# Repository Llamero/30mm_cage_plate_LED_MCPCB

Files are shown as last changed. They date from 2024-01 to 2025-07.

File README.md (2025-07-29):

# 30 mm Cage Plate LED Driver
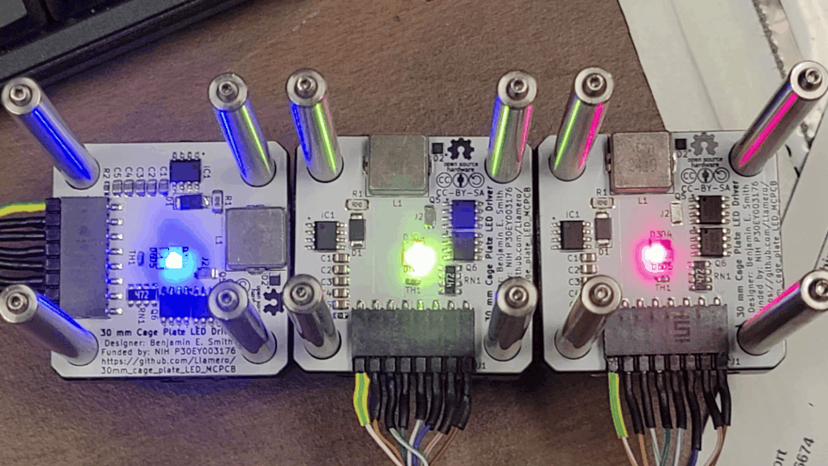
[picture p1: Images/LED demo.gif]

## 4x LED 30 mm Cage Plate Board Description:
This board is an entirely self-contained LED and driver circuitry designed to be compatible with the Thorlabs 30 mm cage plate system: https://www.thorlabs.com/navigation.cfm?guide_id=2004  

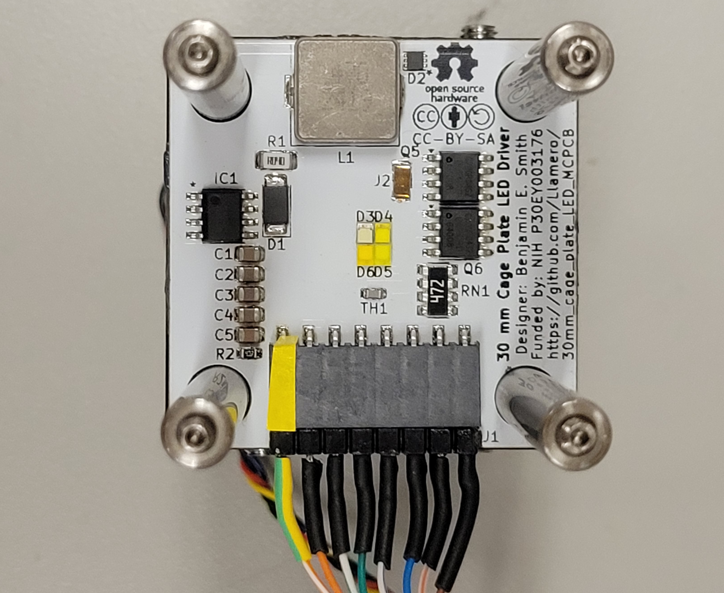
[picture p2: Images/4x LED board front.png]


The LEDs on the board are closely spaced so that all four LEDs efficiently couple into a 5 mm liquid light guide or other optical paths.

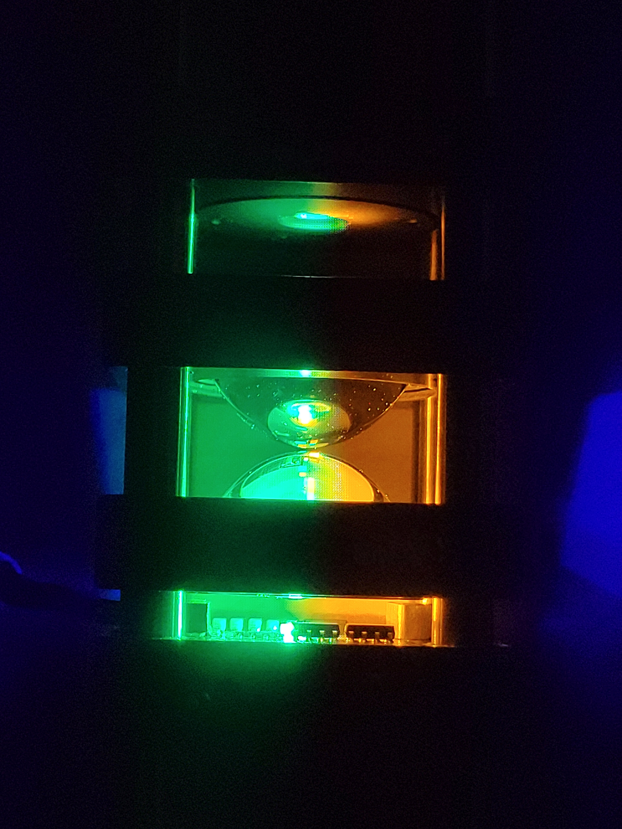
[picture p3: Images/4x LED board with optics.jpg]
Side view of LED with opticas


Each board can drive up to four individual LEDs, and includes a thermistor for temperature monitoring.  The the LED current is regulated by an [AL8843](https://www.diodes.com/part/view/AL8843), allowing LEDs to be driven with up to three amps of current.  The [AL8843](https://www.diodes.com/part/view/AL8843) also allows for both PWM control as well as analog current control down to 10% of the current limit (see below for setting max current limit).

Four p-channel mosfets on the board create a 1x4 multiplexer that allows individual LEDs to be toggled on by pulling the corresponding LED channel's gate to ground.  Each gate has a 4.7 kOhm pullup resistor so that each channel defaults to being off if not connected.

To turn the LEDs off more rapidly, there is also a 38V TVS diode parallel to the inductor that can be used to dump the residual energy stored in the inductor by setting all four multiplexer channels high.

A heatsink and fan can also be mounted to the backside of the cage plate for active cooling of high-current LEDs.

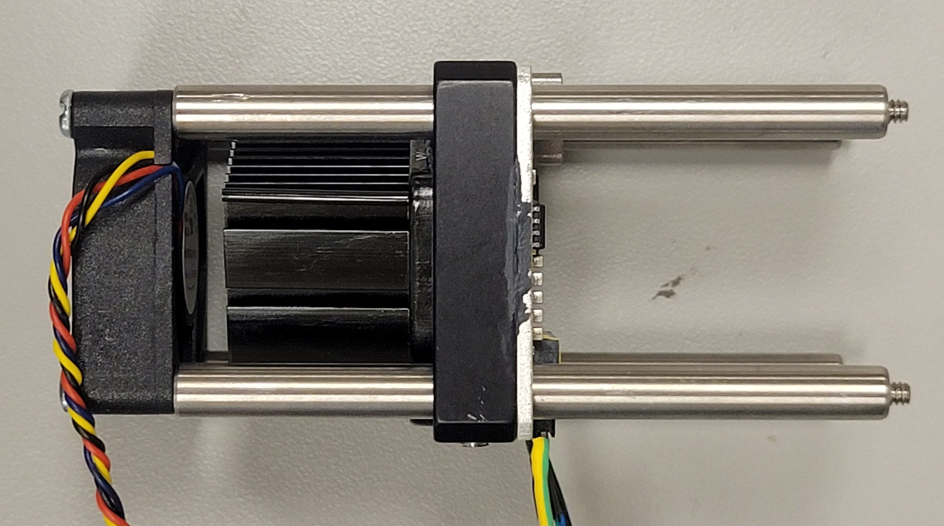
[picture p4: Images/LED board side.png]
Side view of LED driver

## 3x 30 mm Cage Plate Controller Description:
This repository also includes the design files for a controller that can operate up to three 30 mm cage plates for a total of 12 LEDs.

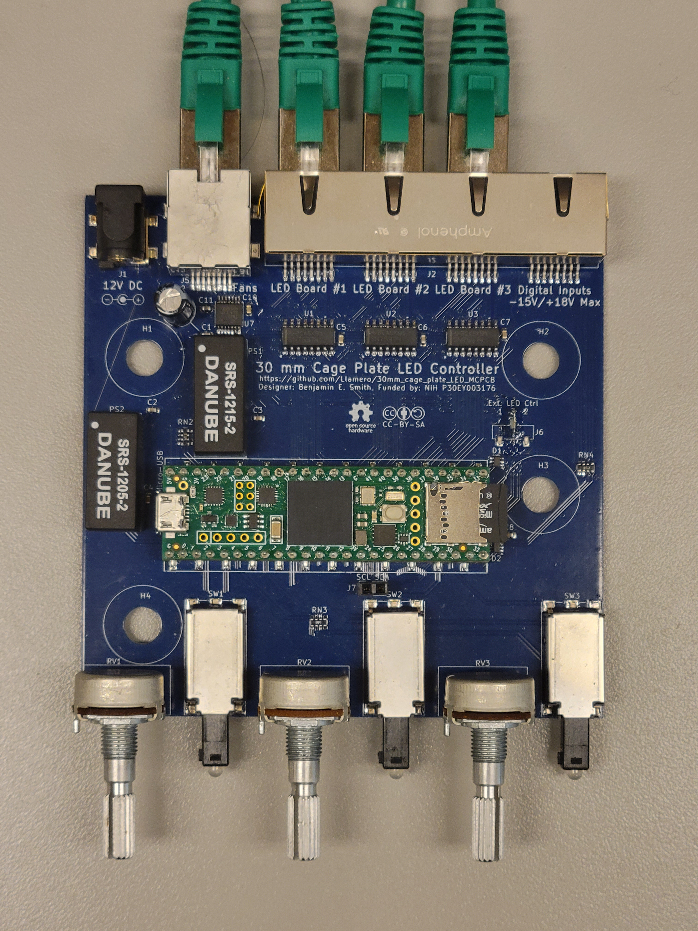
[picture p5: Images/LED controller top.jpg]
LED controller top


The controller is powered by a Teensy 4.1 which allows for precise timing control (<10 ns hysteresis) of each LED, as well a complex programmable control.  

On the back of the driver, each board connects to the driver via a shielded cat5 ethernet cable.  Additionally, there is a cat5 port with both a 12V supply and three channels of 5V PWM outputs for both powering the fans for each board as well as controlling the fan speed.  Finally, there are four protected digital inputs allowing for control signals up to -15V/+18V.

On the front of the driver, there is a potentiometer for controlling the intensity of each of the three LED boards, as well as a pushbutton to select the channel for each board.  Additionally, each pushbutton includes a red-green LED indicator to indicate which of the four LED channels is active.

## Driver Software:
There is software prewritten for the Teensy 4.1 that allows for both manual and programmable control, for syncing to triggers or other inputs.

Additionally, there is a GUI that allows for software control of the LED driver, we well as access to five preset programmable sync modes (digital, analog, confocal, serial, and custom), as well as custom configuration of the LED driver.

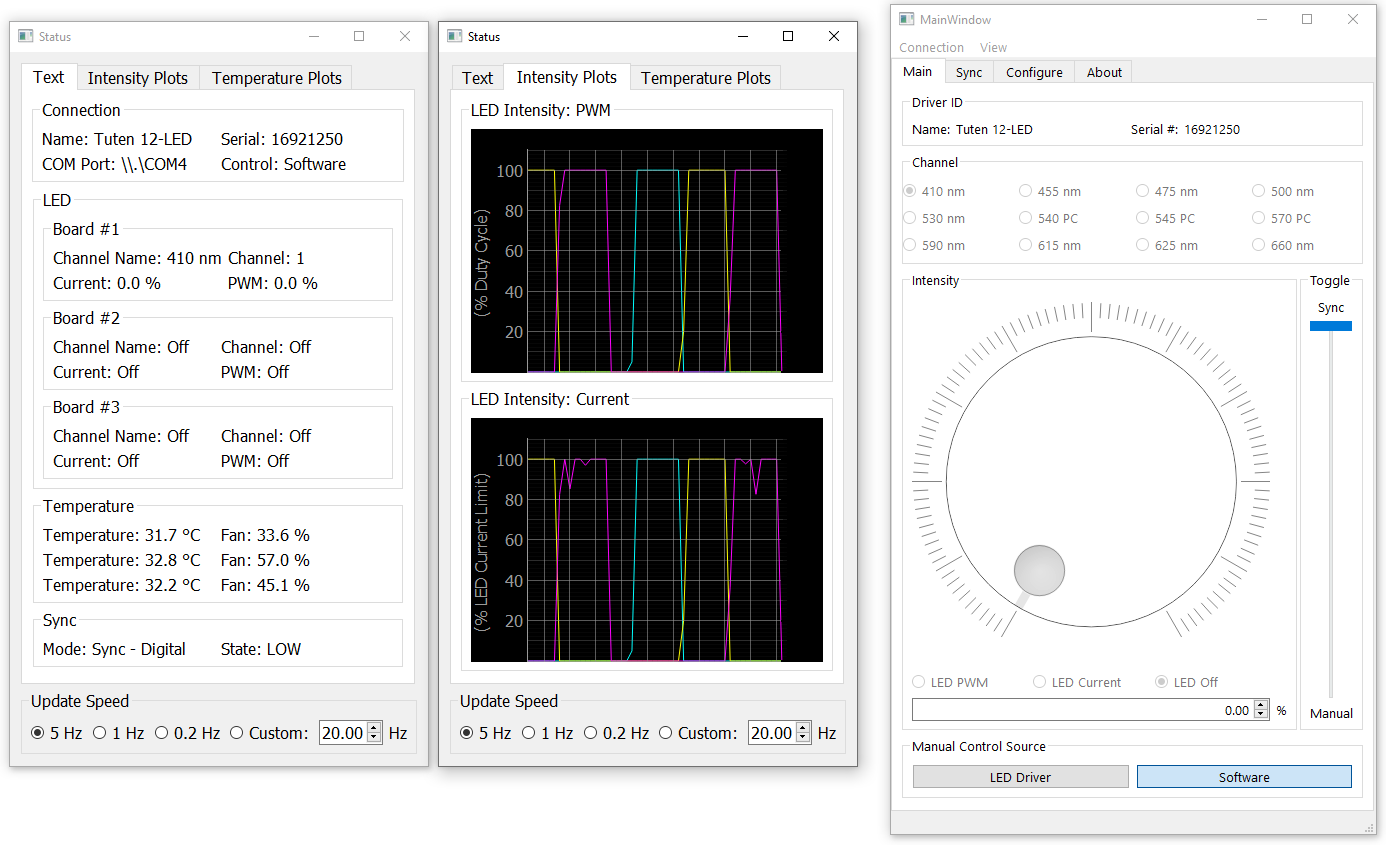
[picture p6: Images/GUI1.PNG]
GUI

## Design:
To view and modify the board, download KiCAD https://www.kicad.org/, and open the project file.

Make sure to modify the LED footprint to match the footprint for your desired LEDs, and to change the current limit resistor to the desired value (see [AL8843](https://www.diodes.com/part/view/AL8843) datasheet, p. 11):
```
RSET (Ω)  Nominal Average Output Current (mA)
0.033     3,000
0.05      2,000
0.067     1,500
0.1       1,000
0.15      667
0.3       333
```
When changing the LED footprints, ensure that the LEDs remain closely spaced for efficient coupling into a liquid light guide.

## Ordering:
The BOM can be found here: 30mm_cage_plate_LED_MCPCB/4x-LED-array/BOM%20-%20Portable%20Tetrachromatic%20Display.xlsx

This BOM includes all the parts needed to build both the LED driver boards as well as the LED controller board.

To order the PCBs, upload the Gerber files to your desired PCB vendor, such as: [https://www.pcbway.com/project/shareproject/W55957ASK98_30_mm_Cage_Plate_LED_MCPCB_kicad_pcb_3d2c1975.html](https://www.pcbway.com/project/shareproject/W55957ASK98_30_mm_Cage_Plate_LED_MCPCB_kicad_pcb_3d2c1975.html)  Make sure that the LED boards are MCPCBs and not FR4.  The driver board can be ordered as an FR4 board.

## Assembly:
To start, spread [thermal epoxy](https://www.digikey.com/en/products/detail/mg-chemicals/8329TCM-6ML/6035511) onto the flat side of a [Thorlabs 30 mm blank cage plate](https://www.thorlabs.com/thorproduct.cfm?partnumber=CP31).

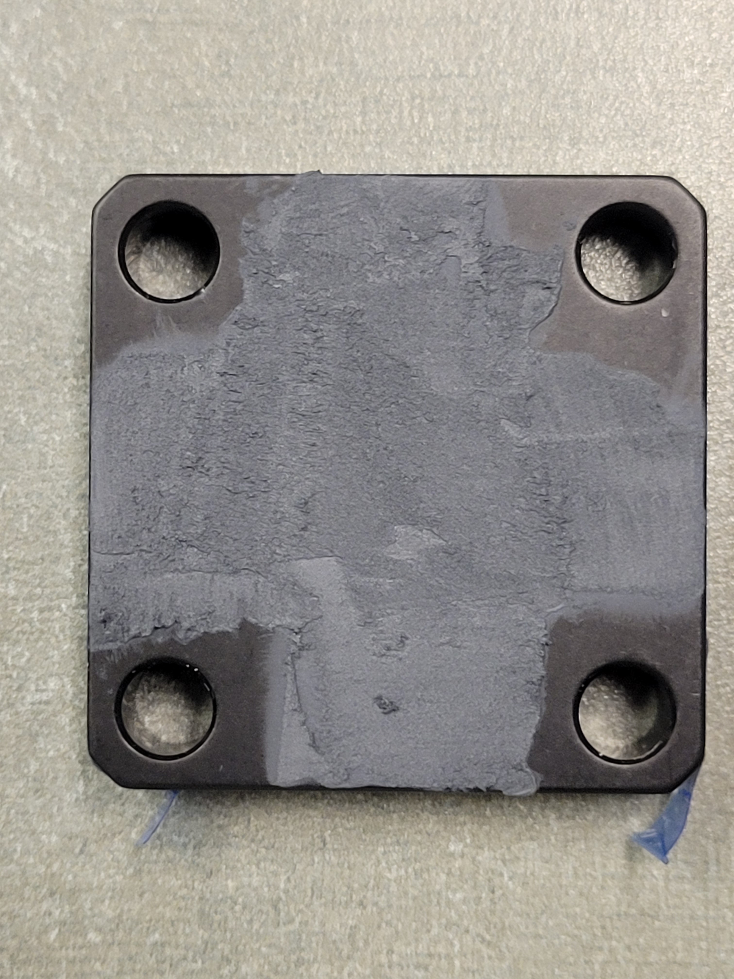
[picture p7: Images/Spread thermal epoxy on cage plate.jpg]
Spread epoxy


Press the MCPCB board firmly to the cage plate using a vise or heavy weights.
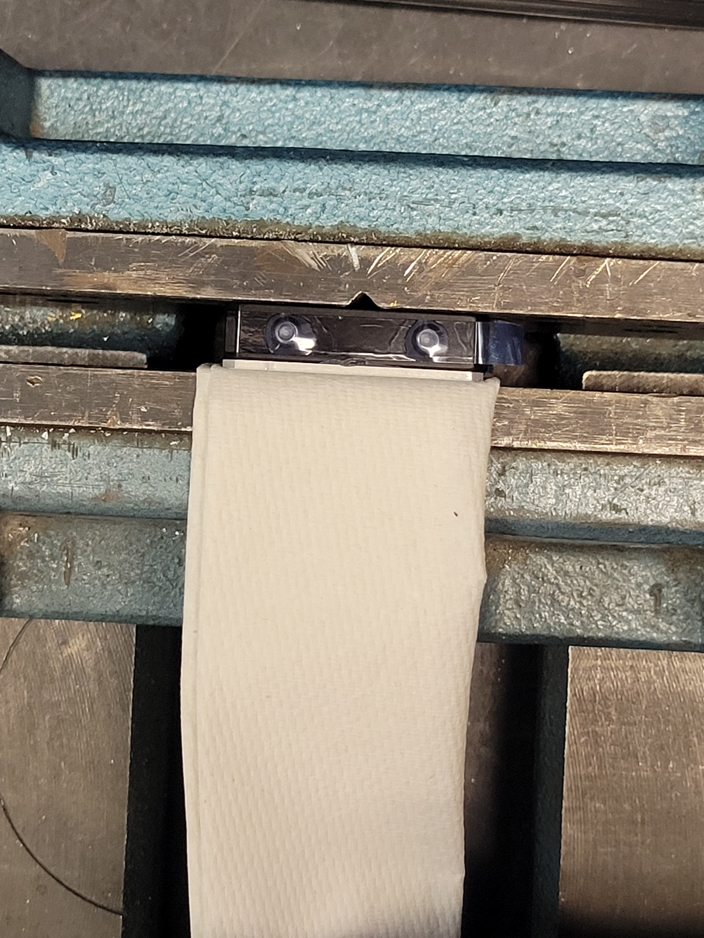
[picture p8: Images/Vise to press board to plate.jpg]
vise


Use a pipette tip or other fine tipped tool to remove excess epoxy from the cage rod holes.
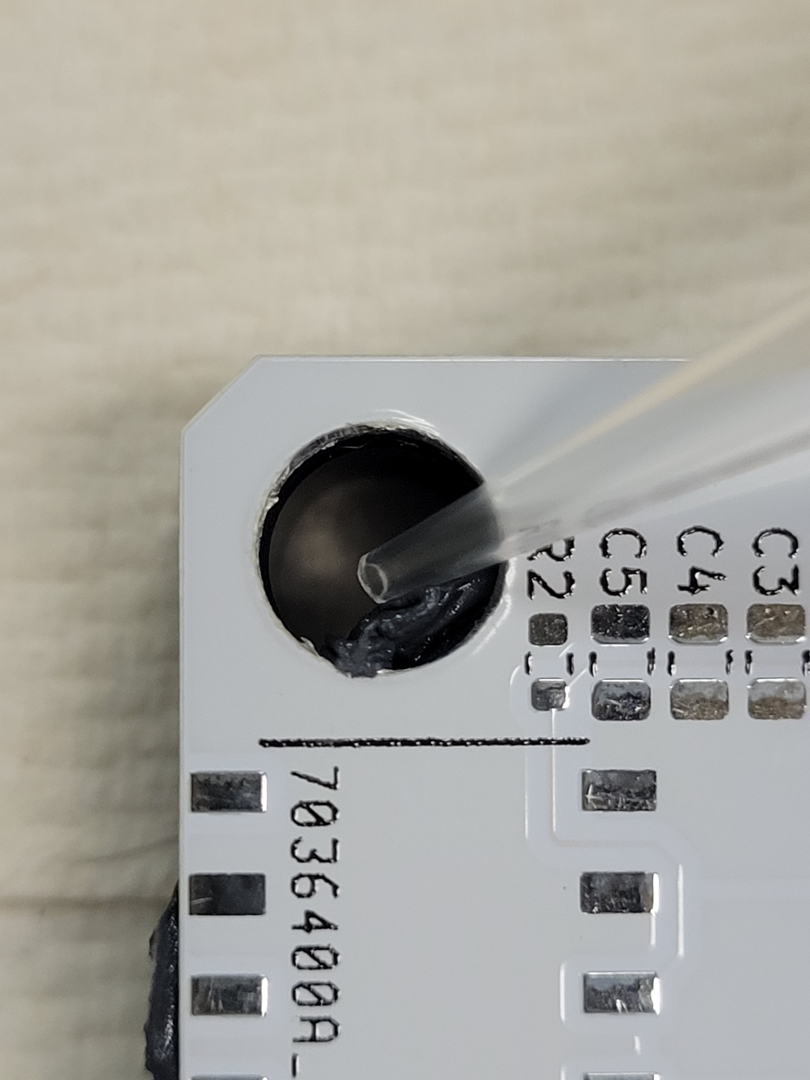
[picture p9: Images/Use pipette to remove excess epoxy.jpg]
Remove excess epoxy


Slide the board across the cage plate as needed to align the cage rod holes and allow the epoxy to cure overnight.

Next, assemble the board similarly to other reflow soldering boards. See the following manual: https://github.com/Llamero/Light_Color_and_Intensity_Datalogger/blob/master/Data%20logger%20assembly%20manual.pdf

Finally, use thermal epoxy to connect the heatsink to the Thorlabs cage plate, press firmly, and bake at 50°C overnight to cure.

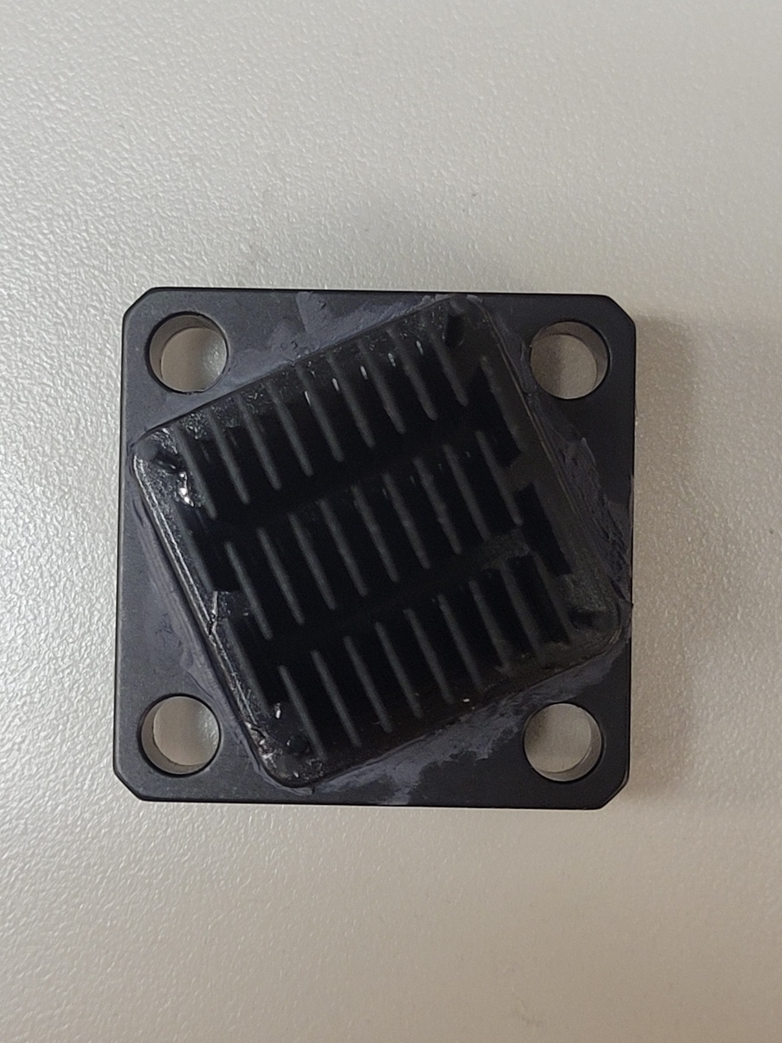
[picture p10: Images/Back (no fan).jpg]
heatsink


## Operation:
Connect a 5V to 20V power supply, with the positive terminal connected to the Vin pin and the negative terminal connected to the Gnd pin. To control the LED current, you can send a +0.4V (10% current) to +2.5V (100% current) to the Ctrl pin. The LED can also be dimmed with PWM with a voltage up to 5V.  To control the mux, pull the channel you want to turn on to ground (0V).  To monitor temperature, measure the resistance of the thermistor.

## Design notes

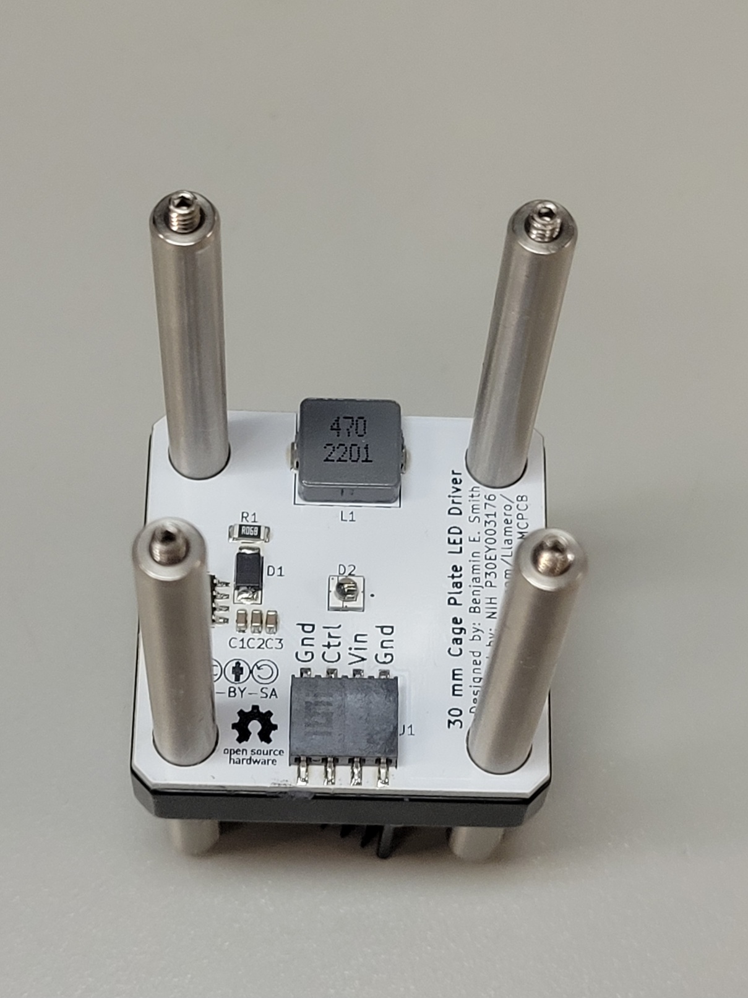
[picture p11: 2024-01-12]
Images/Top with rods.jpg

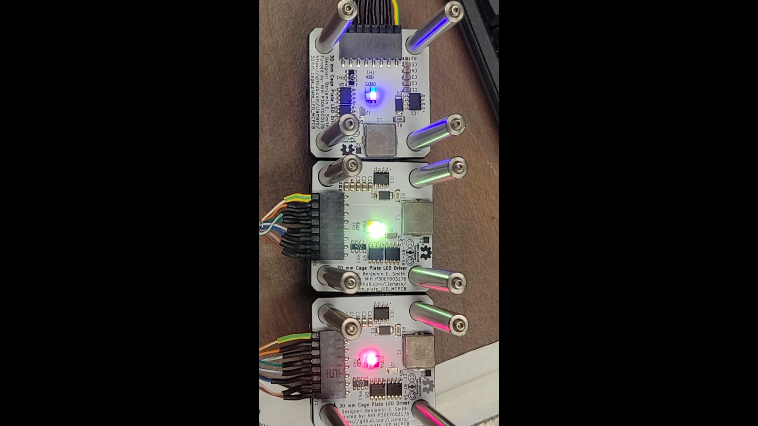
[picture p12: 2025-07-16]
Images/4x LED boards.PNG

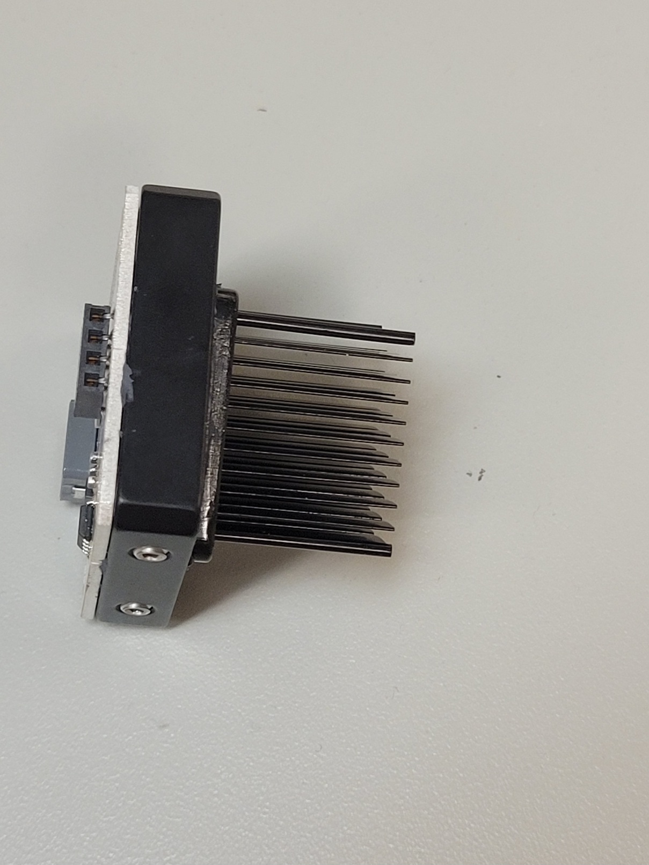
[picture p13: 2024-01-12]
Images/Side.jpg

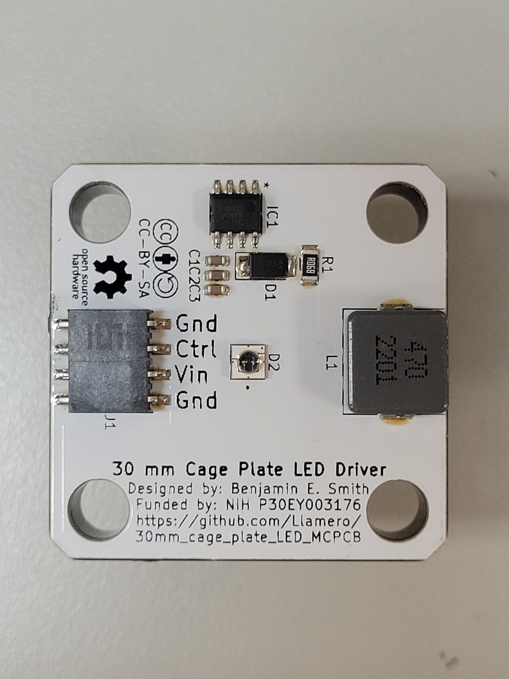
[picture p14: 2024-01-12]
Images/Top.jpg

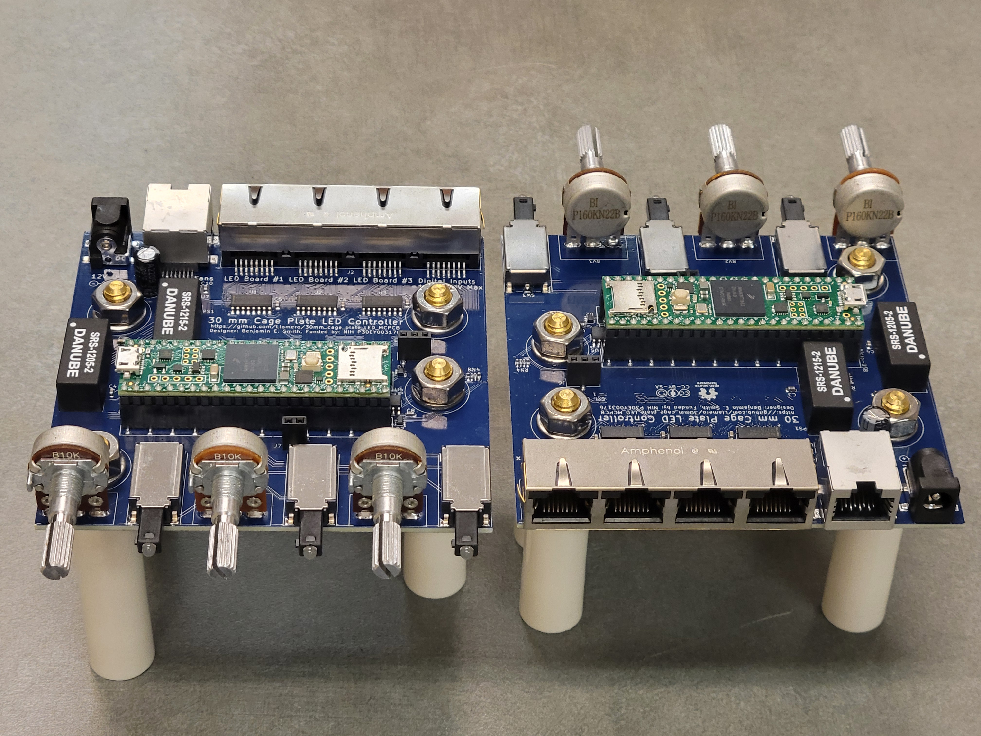
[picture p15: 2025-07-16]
Images/LED controller front and back.jpg

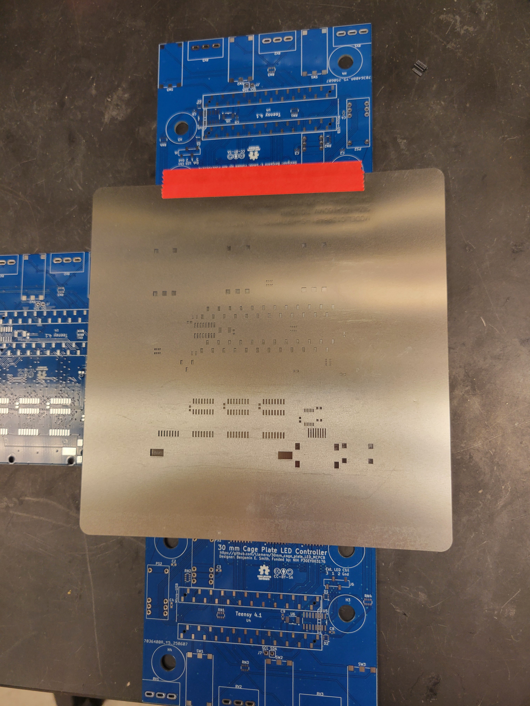
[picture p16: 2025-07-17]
Images/Driver board stencil.jpg

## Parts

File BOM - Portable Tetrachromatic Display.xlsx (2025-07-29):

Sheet: Digikey
Part | Part # | Quantity | Unit Price | Total Price | Link | # Required | Notes | Cust. Ref.
Digikey
LED Controller |  |  |  |  |  |  |  |  | Full Cost | Minimum Cost | Total Cost
CAP ALUM 220UF 20% 25V RADIAL TH | 1189-2913-ND (https://www.digikey.com/en/products/detail/rubycon/25YXJ220M6-3X11/3563124) | 1 | $0.30 | $0.30 | https://www.digikey.com/en/products/detail/rubycon/25YXJ220M6-3X11/3563124 | 1 |  | C12 | $196.03 | $167.16 | $3518.96
CONN MOD JACK 8P8C R/A SHIELDED | RJSSE-5380-04-ND (https://www.digikey.com/en/products/detail/amphenol-cs-commercial-products/RJSSE-5380-04/1242723) | 1 | $7.74 | $7.74 | https://www.digikey.com/en/products/detail/amphenol-cs-commercial-products/RJSSE-5380-04/1242723 | 1 |  | J2
CONN RCPT 24POS 0.1 GOLD SMD | SSM-124-L-SV-LC-ND (https://www.digikey.com/en/products/detail/samtec-inc/SSM-124-L-SV-LC/7861168) | 2 | $4.42 | $8.84 | https://www.digikey.com/en/products/detail/samtec-inc/SSM-124-L-SV-LC/7861168 | 2 |  | J3,J4
CONN HDR 4POS 0.1 GOLD SMD | S5635-ND (https://www.digikey.com/en/products/detail/sullins-connector-solutions/NPPC041KFXC-RC/776094) | 1 | $0.68 | $0.68 | https://www.digikey.com/en/products/detail/sullins-connector-solutions/NPPC041KFXC-RC/776094 | 0 | Ext. LED control | J6
RECEPTACLE STRIP 2P 2.54MM PITCH | 2057-RS1-02-G-ND (https://www.digikey.com/en/products/detail/adam-tech/RS1-02-G/9832044) | 1 | $0.17 | $0.17 | https://www.digikey.com/en/products/detail/adam-tech/RS1-02-G/9832044 | 0 | Audio Tone | J7
BUZZER PIEZO 5V 30MM FLANGE | 458-1251-ND (https://www.digikey.com/en/products/detail/mallory-sonalert-products-inc/PT-2745WQ/1957872) | 1 | $2.04 | $2.04 | https://www.digikey.com/en/products/detail/mallory-sonalert-products-inc/PT-2745WQ/1957872 | 0 | Audio Tone | LS1
PIN HEADER 2.54MM PITCH STR,1X2P | 664-G800W306018EU-ND (https://www.digikey.com/en/products/detail/amphenol-cs-commercial-products/G800W306018EU/13683144) | 1 | $0.10 | $0.10 | https://www.digikey.com/en/products/detail/amphenol-cs-commercial-products/G800W306018EU/13683144 | 0 | Audio Tone | J7-conn
DC DC CONVERTER 15V 1W | 4369-SRS-1215-2-ND (https://www.digikey.com/en/products/detail/diwell-electronics/SRS-1215-2/16572115) | 1 | $1.59 | $1.59 | https://www.digikey.com/en/products/detail/diwell-electronics/SRS-1215-2/16572115 | 1 |  | PS1
DC DC CONVERTER 5V 1W | 4369-SRS-1205-2-ND (https://www.digikey.com/en/products/detail/diwell-electronics/SRS-1205-2/16572067) | 1 | $1.59 | $1.59 | https://www.digikey.com/en/products/detail/diwell-electronics/SRS-1205-2/16572067 | 1 |  | PS2
POT 10K OHM 1/5W PLASTIC LINEAR | 987-1715-ND (https://www.digikey.com/en/products/detail/tt-electronics-bi/P160KN2-0QA25B10K/5957459) | 3 | $1.66 | $4.98 | https://www.digikey.com/en/products/detail/tt-electronics-bi/P160KN2-0QA25B10K/5957459 | 1 | Channel Pot | RV1,RV2,RV3
IC GATE DRVR LOW-SIDE 16SOIC | 296-3362-5-ND (https://www.digikey.com/en/products/detail/texas-instruments/SN75374D/372135) | 3 | $4.47 | $13.41 | https://www.digikey.com/en/products/detail/texas-instruments/SN75374D/372135 | 1 | Channel gate driver | U1,U2,U3
DIODE ARR SCHOT 30V 200MA SOT363 | BAT54BRW-FDICT-ND (https://www.digikey.com/en/products/detail/diodes-incorporated/BAT54BRW-7-F/717700) | 2 | $0.51 | $1.02 | https://www.digikey.com/en/products/detail/diodes-incorporated/BAT54BRW-7-F/717700 | 2 |  | D1,D2
CONN JACK R/A SMT 5.5X2.5MM | 839-54-00165CT-ND (https://www.digikey.com/en/products/detail/tensility-international-corp/54-00165/10459297) | 1 | $0.91 | $0.91 | https://www.digikey.com/en/products/detail/tensility-international-corp/54-00165/10459297 | 1 |  | J1
RES ARRAY 4 RES 3.6K OHM 1206 | 118-CAY16-362J4LFCT-ND (https://www.digikey.com/en/products/detail/bourns-inc/CAY16-362J4LF/2566741) | 3 | $0.10 | $0.30 | https://www.digikey.com/en/products/detail/bourns-inc/CAY16-362J4LF/2566741 | 3 |  | RN1,RN2,RN4
MODULAR JACK - 8P8C, RA, CAT5E, | 664-RJE3A1886102NCT-ND (https://www.digikey.com/en/products/detail/amphenol-cs-commercial-products/RJE3A1886102N/22108417) | 1 | $2.41 | $2.41 | https://www.digikey.com/en/products/detail/amphenol-cs-commercial-products/RJE3A1886102N/22108417 | 1 |  | J5
RES ARRAY 4 RES 390 OHM 1206 | YC164J-390CT-ND (https://www.digikey.com/en/products/detail/yageo/YC164-JR-07390RL/1005113) | 1 | $0.10 | $0.10 | https://www.digikey.com/en/products/detail/yageo/YC164-JR-07390RL/1005113 | 1 |  | RN3
IC TRANSLATOR UNIDIR 14TSSOP | 296-TXU0104PWRCT-ND (https://www.digikey.com/en/products/detail/texas-instruments/TXU0104PWR/14641439) | 1 | $0.77 | $0.77 | https://www.digikey.com/en/products/detail/texas-instruments/TXU0104PWR/14641439 | 1 |  | U7
SWITCH PUSH SPDT 0.25A 50V | CKN10210CT-ND (https://www.digikey.com/en/products/detail/c-k/ELUMOASAQ2C22/2043184) | 3 | $6.81 | $20.43 | https://www.digikey.com/en/products/detail/c-k/ELUMOASAQ2C22/2043184 | 1 | Channel button | SW1,SW2,SW3
IC SWITCH SPDT X 3 75OHM 16SOIC | 296-16708-1-ND (https://www.digikey.com/en/products/detail/texas-instruments/SN74LV4053ADR/614915) | 1 | $0.36 | $0.36 | https://www.digikey.com/en/products/detail/texas-instruments/SN74LV4053ADR/614915 | 1 |  | U5
IC DAC 10BIT V-OUT 10VSSOP | 296-49610-1-ND (https://www.digikey.com/en/products/detail/texas-instruments/DAC104S085QIMMX-NOPB/3871262) | 1 | $5.27 | $5.27 | https://www.digikey.com/en/products/detail/texas-instruments/DAC104S085QIMMX-NOPB/3871262 | 1 |  | U6
CAP CER 1UF 50V X5R 0603 | 587-2400-1-ND (https://www.digikey.com/en/products/detail/taiyo-yuden/UMK107BJ105KA-T/2178919) | 15 | $0.02 | $0.30 | https://www.digikey.com/en/products/detail/taiyo-yuden/UMK107BJ105KA-T/2178919 | 15 |  | C1,C2,C3,C4,C5,C6,C7,C8,C9,C10,C11
HEX SELF THREAD STANDOFF, 1/4 SC | 145-35HSP400-ND (https://www.digikey.com/en/products/detail/essentra-components/35HSP400/11637596) | 4 | $0.25 | $1.00 | https://www.digikey.com/en/products/detail/essentra-components/35HSP400/11637596 | 4 |  | H1,H2,H3,H4
PAN HEAD SLOTTED 1/4"-20 | RPC7320-ND (https://www.digikey.com/en/products/detail/essentra-components/012520P150/9677334) | 4 | $0.25 | $1.00 | https://www.digikey.com/en/products/detail/essentra-components/012520P150/9677334 | 4 |  | H1,H2,H3,H4
CONN HEADER VERT 24POS 2.54MM | S1011EC-24-ND (https://www.digikey.com/en/products/detail/sullins-connector-solutions/PRPC024SAAN-RC/2775230) | 2 | $0.66 | $1.32 | https://www.digikey.com/en/products/detail/sullins-connector-solutions/PRPC024SAAN-RC/2775230 | 2 |  | U4
TEENSY 4.1 | 1568-16771-ND (https://www.digikey.com/en/products/detail/sparkfun-electronics/16771/12180099) | 1 | $31.50 | $31.50 | https://www.digikey.com/en/products/detail/sparkfun-electronics/16771/12180099 | 1 |  | U4
LED Board
HEATSINK 31X31X23MM ELLIPTICAL | 345-1158-ND (https://www.digikey.com/en/products/detail/wakefield-vette/906-31-1-23-2-B-0/4815164) | 1 | $9.28 | $9.28 | https://www.digikey.com/en/products/detail/wakefield-vette/906-31-1-23-2-B-0/4815164 | 1 |  | HS1
CONN HEADER VERT 8POS 2.54MM | 732-5321-ND (https://www.digikey.com/en/products/detail/w%C3%BCrth-elektronik/61300811121/4846839) | 1 | $0.36 | $0.36 | https://www.digikey.com/en/products/detail/w%C3%BCrth-elektronik/61300811121/4846839 | 1 |  | J4
FAN AXIAL 35X10MM 12VDC WIRE | 345-DC0351012W2B-BT0-ND (https://www.digikey.com/en/products/detail/wakefield-vette/DC0351012W2B-BT0/11592900) | 1 | $15.04 | $15.04 | https://www.digikey.com/en/products/detail/wakefield-vette/DC0351012W2B-BT0/11592900 | 1 |  | M2
CAP CER 22UF 25V X5R 0805 | 1276-CL21A226MAYNNNECT-ND (https://www.digikey.com/en/products/detail/samsung-electro-mechanics/CL21A226MAYNNNE/10479857) | 10 | $0.08 | $0.80 | https://www.digikey.com/en/products/detail/samsung-electro-mechanics/CL21A226MAYNNNE/10479857 | 10 |  | C1,C2,C3,C4,C5
TVS DIODE 30VWM 40VC 6DFN | 600-TDS3011P.CCT-ND (https://www.digikey.com/en/products/detail/semtech-corporation/TDS3011P-C/15926911) | 1 | $1.75 | $1.75 | https://www.digikey.com/en/products/detail/semtech-corporation/TDS3011P-C/15926911 | 1 |  | D2
DIODE SCHOTT 100V 3A SOD128/CFP5 | 1727-2397-1-ND (https://www.digikey.com/en/products/detail/nexperia-usa-inc/PMEG10030ELPX/5436251) | 1 | $0.44 | $0.44 | https://www.digikey.com/en/products/detail/nexperia-usa-inc/PMEG10030ELPX/5436251 | 1 |  | D1
IC LED DRIVER RGLTR PWM 3A 8SO | 31-AL8843QSP-13CT-ND (https://www.digikey.com/en/products/detail/diodes-incorporated/AL8843QSP-13/10668306) | 1 | $0.81 | $0.81 | https://www.digikey.com/en/products/detail/diodes-incorporated/AL8843QSP-13/10668306 | 1 |  | IC1
MACH SCREW BINDING SLOTTED #4-40 | RPC7605-ND (https://www.digikey.com/en/products/detail/essentra-components/010440B056/10242213) | 4 | $0.10 | $0.40 | https://www.digikey.com/en/products/detail/essentra-components/010440B056/10242213 | 4 |  | H5,H6,H7,H8
IND,11X10X3.8MM,47UH20%,3.5A,SHD | 118-SRP1038AA-470MCT-ND (https://www.digikey.com/en/products/detail/bourns-inc/SRP1038AA-470M/13910556) | 1 | $1.15 | $1.15 | https://www.digikey.com/en/products/detail/bourns-inc/SRP1038AA-470M/13910556 | 1 |  | L1
CONN RCPT 8POS 0.1 GOLD SMD R/A | SAM14605CT-ND (https://www.digikey.com/en/products/detail/samtec-inc/SSM-108-L-SH-TR/7857935) | 1 | $2.64 | $2.64 | https://www.digikey.com/en/products/detail/samtec-inc/SSM-108-L-SH-TR/7857935 | 1 |  | J1
RES SMD 0 OHM JUMPER 1/2W 1206 | 36-5108CT-ND (https://www.digikey.com/en/products/detail/keystone-electronics/5108/5118869) | 1 | $0.46 | $0.46 | https://www.digikey.com/en/products/detail/keystone-electronics/5108/5118869 | 1 |  | J2
MOSFET 2P-CH 40V 9A 8SOP | 3141-G200P04S2CT-ND (https://www.digikey.com/en/products/detail/goford-semiconductor/G200P04S2/17110013) | 2 | $1.29 | $2.58 | https://www.digikey.com/en/products/detail/goford-semiconductor/G200P04S2/17110013 | 2 |  | Q5,Q6
RES 4.7K OHM 1% 1/10W 0603 | RMCF0603FT4K70CT-ND (https://www.digikey.com/en/products/detail/stackpole-electronics-inc/RMCF0603FT4K70/1760998) | 10 | $0.02 | $0.20 | https://www.digikey.com/en/products/detail/stackpole-electronics-inc/RMCF0603FT4K70/1760998 | 10 |  | R2
THERM NTC 4.7KOHM 3500K 0603 | 490-2439-1-ND (https://www.digikey.com/en/products/detail/murata-electronics/NCP18XM472J03RB/588460) | 2 | $0.15 | $0.30 | https://www.digikey.com/en/products/detail/murata-electronics/NCP18XM472J03RB/588460 | 2 |  | TH1
RES 0.04 OHM 1% 1W 1206 | 13-PE1206FKE470R04ZCT-ND (https://www.digikey.com/en/products/detail/yageo/PE1206FKE470R04Z/) | 1 | $0.26 | $0.26 | https://www.digikey.com/en/products/detail/yageo/PE1206FKE470R04Z/ | 1 |  | R1 - 2.5A limit
XLAMP XEG ROYAL BLUE LED | 90-XEGARY-H2-0000-000-000000K2001CT-ND (https://www.digikey.com/en/products/detail/cree-led/XEGARY-H2-0000-000-000000K2001/) | 1 | $2.16 | $2.16 | https://www.digikey.com/en/products/detail/cree-led/XEGARY-H2-0000-000-000000K2001/ | 1 |  | D3
XLAMP XEG GREEN LED | 90-XEGAGR-H2-0000-000-000000T6001CT-ND (https://www.digikey.com/en/products/detail/cree-led/XEGAGR-H2-0000-000-000000T6001/) | 1 | $2.16 | $2.16 | https://www.digikey.com/en/products/detail/cree-led/XEGAGR-H2-0000-000-000000T6001/ | 1 |  | D4
XLAMP XEG AMBER LED | 90-XEGAAM-H2-0000-000-000000Q5001CT-ND (https://www.digikey.com/en/products/detail/cree-led/XEGAAM-H2-0000-000-000000Q5001/) | 1 | $2.30 | $2.30 | https://www.digikey.com/en/products/detail/cree-led/XEGAAM-H2-0000-000-000000Q5001/ | 1 |  | D5
XLAMP XEG RED LED | 90-XEGARD-H2-0000-000-000000R5001CT-ND (https://www.digikey.com/en/products/detail/cree-led/XEGARD-H2-0000-000-000000R5001/) | 1 | $2.88 | $2.88 | https://www.digikey.com/en/products/detail/cree-led/XEGARD-H2-0000-000-000000R5001/ | 1 |  | D6
Cables
CABLE MOD 8P8C PLUG-PLUG 6.56' | AE10195-ND (https://www.digikey.com/en/products/detail/assmann-wsw-components/A-MCSSP60020-B/1218996) | 1 | $8.79 | $8.79 | https://www.digikey.com/en/products/detail/assmann-wsw-components/A-MCSSP60020-B/1218996 | 1 |  | J3
CABLE MOD 8P8C PLUG-PLUG 3.28' | AE9961-ND (https://www.digikey.com/en/products/detail/assmann-wsw-components/A-MCSP-80010/821715) | 1 | $3.64 | $3.64 | https://www.digikey.com/en/products/detail/assmann-wsw-components/A-MCSP-80010/821715 | 1 |  | FAN CABLE
JUMPER SPHD-001T-P0.5 X2 12" | 455-3086-ND (https://www.digikey.com/en/products/detail/jst-sales-america-inc/APAPA22K305/6009462) | 7 | $0.47 | $3.29 | https://www.digikey.com/en/products/detail/jst-sales-america-inc/APAPA22K305/6009462 | 7 |  | DLP WIRE
SHUNT MOD.IV OPEN-TOP 2POS | A106575-ND (https://www.digikey.com/en/products/detail/te-connectivity-amp-connectors/142270-5/2055476) | 1 | $0.84 | $0.84 | https://www.digikey.com/en/products/detail/te-connectivity-amp-connectors/142270-5/2055476 | 1 |  | DLP JUMPER
IC GATE DRVR LOW-SIDE 14DIP | 576-2334-ND (https://www.digikey.com/en/products/detail/microchip-technology/MIC4468YN/1616912) | 1 | $5.32 | $5.32 | https://www.digikey.com/en/products/detail/microchip-technology/MIC4468YN/1616912 | 1 |  | GATE DRIVER
CAP CER 10UF 25V X5R RADIAL | 445-181284-1-ND (https://www.digikey.com/en/products/detail/tdk-corporation/FG28X5R1E106MRT06/10185405) | 1 | $0.45 | $0.45 | https://www.digikey.com/en/products/detail/tdk-corporation/FG28X5R1E106MRT06/10185405 | 1 |  | BYPASS CAP
RES ARRAY 4 RES 4.7K OHM 2012 | 13-YC324-FK-074K7LCT-ND (https://www.digikey.com/en/products/detail/yageo/YC324-FK-074K7L/5953850) | 2 | $0.32 | $0.64 | https://www.digikey.com/en/products/detail/yageo/YC324-FK-074K7L/5953850 | 2 |  | RN1
CONN RCPT HSG 14POS 2.00MM | 455-1172-ND (https://www.digikey.com/en/products/detail/jst-sales-america-inc/PHDR-14VS/608614) | 1 | $0.29 | $0.29 | https://www.digikey.com/en/products/detail/jst-sales-america-inc/PHDR-14VS/608614 | 1
Hardware
Foot Cylindrical, Recessed Center 0.710" Dia | 3720-2545-ND (https://www.digikey.com/en/products/detail/heyco-products-corporation/2545/15906485) | 4 | $0.47 | $1.88 | https://www.heyco.com/wp-content/uploads/2024/09/Feets-Of-Strength-FSD-FSS.pdf | 4
WASHER FLAT RETAINING 1/4" NYLON | RPC9970-ND (https://www.digikey.com/en/products/detail/essentra-components/16FWRT250032A/10298866) | 10 | $0.08 | $0.77 | https://www.digikey.com/en/products/detail/essentra-components/16FWRT250032A/10298866 | 10
JAM NUT 7/16" NYLON 1/4"-20 | RPC8589-ND (https://www.digikey.com/en/products/detail/essentra-components/0425020HJN/10243197) | 10 | $0.25 | $2.46 | https://www.digikey.com/en/products/detail/essentra-components/0425020HJN/10243197 | 10
CBL USB2.0 A PLUG-MIN A PLUG 6' | 380-1429-ND (https://www.digikey.com/en/products/detail/stewart-connector/SC-2ANK006F/8544575) | 1 | $3.27 | $3.27 | https://www.digikey.com/en/products/detail/stewart-connector/SC-2ANK006F/8544575 | 1
CBL USB2.0 A PLUG-MCR B PLUG 6' | 380-1432-ND (https://www.digikey.com/en/products/detail/stewart-connector/SC-2AMK006F/8544578) | 1 | $3.12 | $3.12 | https://www.digikey.com/en/products/detail/stewart-connector/SC-2AMK006F/8544578 | 1
CABLE M-M HDMI-A 6' SHLD | 5181-HDMI-MM-06F-ND (https://www.digikey.com/en/products/detail/unc-group-llc/HDMI-MM-06F/12759709) | 1 | $7.17 | $7.17 | https://www.digikey.com/en/products/detail/unc-group-llc/HDMI-MM-06F/12759709 | 1

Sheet: Amazon
Part | Part # | Quantity | Unit Price | Total Price | Link | # Required | Notes | Cust. Ref.
Amazon
ALITOVE DC 12V 5A Power Supply Adapter Converter Transformer AC 100-240V Input with 5.5x2.5mm | B01GEA8PQA | 1 | $11.99 | $11.99 | https://www.amazon.com/dp/B01GEA8PQA | 1 |  |  | Full Cost | Minimum Cost
Micro USB Cable Android Charger 6ft 2PACK | B0D7RZJSPS | 1 | $4.99 | $4.99 | https://www.amazon.com/dp/B0D7RZJSPS | 1 |  |  | $125.63 | $125.63
SanDisk 64GB Ultra microSDXC UHS-I Memory Card | B0B7NXBM6P | 1 | $7.41 | $7.41 | https://www.amazon.com/dp/B0B7NXBM6P | 1
Painted Steel, 12" x 12" x 6",Gray | B00PSMY77W | 1 | $49.51 | $49.51 | https://www.amazon.com/Wiegmann-SC121206NK-Wallmount-Knockouts-Painted/dp/B00PSMY77W | 1
(20Sets) 1/4-20 Bolt x 3/8" Button Head Socket Cap Bolts, Black Oxide | B0D91FMDVY | 1 | $9.99 | $9.99 | https://www.amazon.com/20Sets-Stainless-Assortment-Threaded-Spanner/dp/B0D91FMDVY | 1
Mini HDMI Male to HDMI 2.0 Female Mount | B0CB7FPMCZ | 1 | $14.99 | $14.99 | https://www.amazon.com/QIANRENON-Threaded-Waterproof-Extension-Camcorder/dp/B0CB7FPMCZ | 1
Mini USB 5Pin Flush Mount Male to Female Extension | B0BMF91BCQ | 1 | $8.88 | $8.88 | https://www.amazon.com/chenyang-Waterproof-Female-Extension-Dustproof/dp/B0BMF91BCQ | 1
3 Sets 5.5 x 2.5 MM 10A DC Power Jack Socket Threaded Female Mount Connector | B0B6FFN4V5 | 1 | $8.99 | $8.99 | https://www.amazon.com/SDTC-Tech-Threaded-Connector-Dustproof/dp/B0B6FFN4V5 | 1
Micro USB 5Pin Flush Mount Male to Female Extension Cable | B0BMDSHJ88 | 1 | $8.88 | $8.88 | https://www.amazon.com/chenyang-Waterproof-Female-Extension-Dustproof/dp/B0BMDSHJ88 | 1
 |  |  |  |  |  | 0
 |  |  |  |  |  | 0
 |  |  |  |  |  | 0
 |  |  |  |  |  | 0
 |  |  |  |  |  | 0
 |  |  |  |  |  | 0
 |  |  |  |  |  | 0
 |  |  |  |  |  | 0
 |  |  |  |  |  | 0
 |  |  |  |  |  | 0
 |  |  |  |  |  | 0
 |  |  |  |  |  | 0
 |  |  |  |  |  | 0
 |  |  |  |  |  | 0
 |  |  |  |  |  | 0
 |  |  |  |  |  | 0
 |  |  |  |  |  | 0
 |  |  |  |  |  | 0
 |  |  |  |  |  | 0
 |  |  |  |  |  | 0
 |  |  |  |  |  | 0
 |  |  |  |  |  | 0
 |  |  |  |  |  | 0
 |  |  |  |  |  | 0
 |  |  |  |  |  | 0
 |  |  |  |  |  | 0
 |  |  |  |  |  | 0
 |  |  |  |  |  | 0
 |  |  |  |  |  | 0
 |  |  |  |  |  | 0
 |  |  |  |  |  | 0
 |  |  |  |  |  | 0
 |  |  |  |  |  | 0
 |  |  |  |  |  | 0
 |  |  |  |  |  | 0
 |  |  |  |  |  | 0
 |  |  |  |  |  | 0
 |  |  |  |  |  | 0

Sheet: Thorlabs
Part | Part # | Quantity | Unit Price | Total Price | Link | # Required | Notes | Cust. Ref.
Thorlabs
Ø1" Pillar Post, 1/4"-20 Taps, L = 2" | RS2 | 2 | $29.35 | $58.70 | https://www.thorlabs.com/thorproduct.cfm?partnumber=RS2 | 2 |  |  | Full Cost | Minimum Cost
Cage Plate Mounting Base for 30 mm Cage Plates, Imperial | CPB1 | 1 | $19.92 | $19.92 | https://www.thorlabs.com/thorproduct.cfm?partnumber=CPB1 | 1 |  |  | $853.40 | $853.40
Cage Assembly Rod, 4" Long, Ø6 mm, 4 Pack | ER4-P4 | 1 | $31.22 | $31.22 | https://www.thorlabs.us/thorproduct.cfm?partnumber=ER4-P4 | 1
Liquid Light Guide, Ø5 mm Core, 340 - 800 nm, 4' (1.2 m) Length | LLG05-4H | 1 | $577.06 | $577.06 | https://www.thorlabs.us/thorproduct.cfm?partnumber=LLG05-4H | 1
Ø5 mm LLG to SM1 Adapter | AD5LLG | 1 | $41.00 | $41.00 | https://www.thorlabs.us/thorproduct.cfm?partnumber=AD5LLG | 1
SM1-Threaded 30 mm Cage Plate, 0.35" Thick, 2 Retaining Rings, 8-32 Tap | CP33 | 3 | $20.43 | $61.29 | https://www.thorlabs.us/thorproduct.cfm?partnumber=CP33 | 3
Aspheric Condenser Lens, Ø1", f=16 mm, NA=0.79, Uncoated | ACL25416U | 2 | $22.00 | $44.00 | https://www.thorlabs.us/thorproduct.cfm?partnumber=ACL25416U | 2
Blank 30 mm Cage Plate, 0.35" Thick, 8-32 Tap | CP31 | 1 | $20.21 | $20.21 | https://www.thorlabs.us/thorproduct.cfm?partnumber=CP31 | 1
 |  |  |  |  |  | 0
 |  |  |  |  |  | 0
 |  |  |  |  |  | 0
 |  |  |  |  |  | 0
 |  |  |  |  |  | 0
 |  |  |  |  |  | 0
 |  |  |  |  |  | 0
 |  |  |  |  |  | 0
 |  |  |  |  |  | 0
 |  |  |  |  |  | 0
 |  |  |  |  |  | 0
 |  |  |  |  |  | 0
 |  |  |  |  |  | 0
 |  |  |  |  |  | 0
 |  |  |  |  |  | 0
 |  |  |  |  |  | 0
 |  |  |  |  |  | 0
 |  |  |  |  |  | 0
 |  |  |  |  |  | 0
 |  |  |  |  |  | 0
 |  |  |  |  |  | 0
 |  |  |  |  |  | 0
 |  |  |  |  |  | 0
 |  |  |  |  |  | 0
 |  |  |  |  |  | 0
 |  |  |  |  |  | 0
 |  |  |  |  |  | 0
 |  |  |  |  |  | 0
 |  |  |  |  |  | 0
 |  |  |  |  |  | 0
 |  |  |  |  |  | 0
 |  |  |  |  |  | 0
 |  |  |  |  |  | 0
 |  |  |  |  |  | 0
 |  |  |  |  |  | 0
 |  |  |  |  |  | 0
 |  |  |  |  |  | 0
 |  |  |  |  |  | 0
 |  |  |  |  |  | 0

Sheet: EKB
Part | Part # | Quantity | Unit Price | Total Price | Link | # Required | Notes | Cust. Ref.
EKB
DLP® LightCrafter™ Fiber-E4500MKIITM | DPM-E4500MKIIFC | 1 | $2343.90 | $2343.90 | https://www.thorlabs.com/thorproduct.cfm?partnumber=RS2 | 1 |  |  | Full Cost | Minimum Cost
 |  |  |  |  |  |  |  |  | $2343.90 | $2343.90
 |  |  |  |  |  | 0
 |  |  |  |  |  | 0
 |  |  |  |  |  | 0
 |  |  |  |  |  | 0
 |  |  |  |  |  | 0
 |  |  |  |  |  | 0
 |  |  |  |  |  | 0
 |  |  |  |  |  | 0
 |  |  |  |  |  | 0
 |  |  |  |  |  | 0
 |  |  |  |  |  | 0
 |  |  |  |  |  | 0
 |  |  |  |  |  | 0
 |  |  |  |  |  | 0
 |  |  |  |  |  | 0
 |  |  |  |  |  | 0
 |  |  |  |  |  | 0
 |  |  |  |  |  | 0
 |  |  |  |  |  | 0
 |  |  |  |  |  | 0
 |  |  |  |  |  | 0
 |  |  |  |  |  | 0
 |  |  |  |  |  | 0
 |  |  |  |  |  | 0
 |  |  |  |  |  | 0
 |  |  |  |  |  | 0
 |  |  |  |  |  | 0
 |  |  |  |  |  | 0
 |  |  |  |  |  | 0
 |  |  |  |  |  | 0
 |  |  |  |  |  | 0
 |  |  |  |  |  | 0
 |  |  |  |  |  | 0
 |  |  |  |  |  | 0
 |  |  |  |  |  | 0
 |  |  |  |  |  | 0
 |  |  |  |  |  | 0
 |  |  |  |  |  | 0
 |  |  |  |  |  | 0

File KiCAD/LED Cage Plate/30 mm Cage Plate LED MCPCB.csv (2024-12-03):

Reference | Value | Datasheet | Footprint | Qty | DNP | Manufacturer | Part
C1,C2,C3,C4,C5 | 22μF | https://mm.digikey.com/Volume0/opasdata/d220001/medias/docus/339/CL21A226MAYNNNE_Spec.pdf | Capacitor_SMD:C_0805_2012Metric | 5 |  | Samsung Electro-Mechanics | CL21A226MAYNNNE
D1 | D_Schottky | https://assets.nexperia.com/documents/data-sheet/PMEG10030ELP.pdf | Custom:D_SOD-128 | 1 |  | Nexperia USA Inc. | PMEG10030ELPX
D2 | D_Zener | https://semtech.my.salesforce.com/sfc/p/ | Custom:DFN6_TDS3011_SEM | 1 |  | Semtech Corporation | TDS3011P.C
D3,D4,D5,D6 | LED_Pad | https://downloads.cree-led.com/files/ds/x/XLamp-XE-G.pdf | Custom:LED_XLAMP_XE-G_CRW | 4 |  | Cree LED | XEGAGR-H0-0000-000-000000T6001
H5,H6,H7,H8 | MountingHole | https://www.keyelco.com/userAssets/file/M65p135.pdf |  | 4 |  | Keystone Electronics | 9302
HS1 | Heatsink | https://wakefieldthermal.com/content/data_sheets/ELLIPTICAL%20FIN%20HEAT%20SINK.pdf |  | 1 |  | Wakefield-Vette | 906-31-1-23-2-B-0
IC1 | AL8843QSP-13 | https://www.diodes.com/assets/Datasheets/AL8843Q.pdf | Custom:SO-8EP_3P9X4P95_DIO | 1 |  | Diodes Incorporated | AL8843QSP-13
J1 | Conn_01x08_Socket | https://mm.digikey.com/Volume0/opasdata/d220001/medias/docus/6129/ssm-1xx-xxx-xx-xx-xx-xx-x-xx-mkt.pdf | Custom:SAMTEC_SSM-108-F-SH-TR | 1 |  | Samtec Inc. | SSM-108-F-SH-TR
J2 | 0 | https://www.keyelco.com/userAssets/file/M65p54.pdf | Resistor_SMD:R_1206_3216Metric | 1 |  | Keystone Electronics | 5104
J3 | RJ45_Shielded | https://www.assmann-wsw.com/uploads/datasheets/ASS_7946_CA.pdf |  | 1 |  | Assmann WSW Components | AMJF0808-0100-GNB-26
J4 | Conn_01x08_Pin | https://www.we-online.com/components/products/datasheet/61300811121.pdf |  | 1 |  | Würth Elektronik | 61300811121
L1 | 47μH | https://www.bourns.com/docs/Product-Datasheets/SRP1038A.pdf | Custom:SRP1038A-220M_BRN | 1 |  | Bourns Inc. | SRP1038AA-470M
M2 | Fan_4pin | https://wakefieldthermal.com/content/data_sheets/wfv-dc-fans-rev-a3%20%281%29.pdf |  | 1 |  | Wakefield-Vette | DC0351012W2B-BT0
Q5,Q6 | 2x_p-channel | -- mixed values -- | Custom:SOP-8_3.9x4.9mm_P1.27mm | 2 |  | Goford Semiconductor | G200P04S2
R1 | 0.040 | https://mm.digikey.com/Volume0/opasdata/d220001/medias/docus/5343/PE_Series_DS.pdf | Resistor_SMD:R_1206_3216Metric | 1 |  | YAGEO | PE1206FKE470R04Z
R2 | 4700 | https://www.seielect.com/catalog/sei-rmcf_rmcp.pdf | Resistor_SMD:R_0603_1608Metric | 1 |  | Stackpole Electronics Inc | RMCF0603FT4K70
RN1 | 4700 | https://www.yageo.com/upload/media/product/app/datasheet/rchip/pyu-yc_tc_group_51_rohs_l.pdf | Resistor_SMD:R_Array_Convex_4x1206 | 1 |  | YAGEO | YC324-JK-074K7L
TH1 | Thermistor | https://www.murata.com/products/productdata/8796839149598/NTHCG158.txt?1437969900000 | Resistor_SMD:R_0603_1608Metric | 1 |  | Murata Electronics | NCP18XM472J03RB

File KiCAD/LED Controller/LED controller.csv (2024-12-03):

Reference | Value | Datasheet | Footprint | Qty | DNP | Manufacturer | Part | Description
C1,C2,C3,C4,C5,C6,C7,C8,C9,C10,C11 | 1µF | https://mm.digikey.com/Volume0/opasdata/d220001/medias/docus/658/CL10A105KB8NNNC_Spec.pdf | Capacitor_SMD:C_0603_1608Metric | 11 |  | Samsung Electro-Mechanics | CL10A105KB8NNNC | CAP CER 1UF 50V X5R 0603
C12 | 220µF | https://www.rubycon.co.jp/wp-content/uploads/catalog-aluminum/YXJ.pdf | Capacitor_THT:CP_Radial_D6.3mm_P2.50mm | 1 |  | Rubycon | 25YXJ220M6.3X11 | CAP ALUM 220UF 20% 25V RADIAL TH
D1,D2 | BAT54BRW | https://www.diodes.com/assets/Datasheets/ds30152.pdf | Package_TO_SOT_SMD:SOT-363_SC-70-6 | 2 |  | Diodes Incorporated | BAT54BRW-7-F | DIODE ARR SCHOT 30V 200MA SOT363
J1 | Barrel_Jack_Switch | https://tensility.s3-us-west-2.amazonaws.com/uploads/product_doc/document/4054/54-00165.pdf | Custom Footprints:DC-jack_54-00165 | 1 |  | Tensility International Corp | 54-00165
J2 | 4x RJ45 | https://cdn.amphenol-cs.com/media/wysiwyg/files/drawing/rjsse538004.pdf | Custom Footprints:RJ45_x4-RJSSE-5380-04 | 1 |  | Amphenol ICC (Commercial Products) | RJSSE-5380-04 | CONN MOD JACK 8P8C R/A SHIELDED
J3,J4 | Conn_01x24_Female | https://www.samtec.com/partnumber/ssm-124-l-sv-lc?vendor=digikey |  | 2 |  | Samtec Inc. | SSM-124-L-SV-LC | CONN RCPT 24POS 0.1 GOLD SMD
J5 | 8P8C_Shielded | https://cdn.amphenol-cs.com/media/wysiwyg/files/drawing/p-rje3b-188-6x02-n.pdf | Custom Footprints:1x RJ45 | 1 |  | Amphenol ICC (Commercial Products) | RJE3A1886102N | MODULAR JACK - 8P8C, RA, CAT5E,
J6 | Conn_01x03_Socket | https://cdn.harwin.com/pdfs/M20-786.pdf | Connector_PinSocket_2.54mm:PinSocket_1x03_P2.54mm_Vertical_SMD_Pin1Left | 1 |  | Harwin Inc. | M20-7860346 | CONN RCPT 3POS 0.1 TIN SMD
J7 | Conn_01x02_Socket | https://app.adam-tech.com/products/download/data_sheet/203013/rs1-xx-g-data-sheet.pdf | Connector_PinSocket_2.54mm:PinSocket_1x02_P2.54mm_Vertical | 1 |  | Adam Tech | RS1-02-G | RECEPTACLE STRIP 2P 2.54MM PITCH
LS1 | Speaker | https://mspindy.com/technical-guides/transducers-external-drive-piezo/ |  | 1 |  | Mallory Sonalert Products Inc. | PT-2745WQ | BUZZER PIEZO 5V 30MM FLANGE
PS1 | 15V DC-DC | http://diwellshop.cafe24.com/web/DATASHEET/01_subtitle/4_POWER/2_DC-DC/SRS-1212-2/SR.pdf | Custom Footprints:SRS-1215-2 | 1 |  | Diwell Electronics | SRS-1215-2 | DC DC CONVERTER 15V 1W
PS2 | 15V DC-DC | http://diwellshop.cafe24.com/web/DATASHEET/01_subtitle/4_POWER/2_DC-DC/SRS-1212-2/SR.pdf | Custom Footprints:SRS-1215-2 | 1 |  | Diwell Electronics | SRS-1205-2 | DC DC CONVERTER 5V 1W
RN1,RN2,RN4 | 3600 | https://www.bourns.com/docs/Product-Datasheets/CATCAY.pdf | Resistor_SMD:R_Array_Convex_4x0603 | 3 |  | Bourns Inc. | CAY16-362J4LF | RES ARRAY 4 RES 3.6K OHM 1206
RN3 | 390 | https://www.yageo.com/upload/media/product/app/datasheet/rchip/pyu-yc_tc_group_51_rohs_l.pdf | Resistor_SMD:R_Array_Convex_4x0603 | 1 |  | YAGEO | YC164-JR-07390RL | RES ARRAY 4 RES 390 OHM 1206
RV1,RV2,RV3 | 10k | https://www.ttelectronics.com/TTElectronics/media/ProductFiles/Datasheet/P160.pdf | Custom Footprints:P160KN2-4QC20B10K | 3 |  | TT Electronics/BI | P160KN2-0QA25B10K | POT 10K OHM 1/5W PLASTIC LINEAR
SW1,SW2,SW3 | ELUMOASAQ2C22 | https://www.ckswitches.com/media/1405/elum.pdf | Custom Footprints:ELUMOASAQ2C22_CNK | 3 |  | C&K | ELUMOASAQ2C22 | SWITCH PUSH SPDT 0.25A 50V
U1,U2,U3 | 4x Gate Driver | https://www.ti.com/general/docs/suppproductinfo.tsp?distId=10 | Custom Footprints:D16-4x gate driver | 3 |  | Texas Instruments | SN75374D | IC GATE DRVR LOW-SIDE 16SOIC
U4 | Teensy4.1 | https://mm.digikey.com/Volume0/opasdata/d220001/medias/docus/2942/DEV-16996_Web.pdf | Custom Footprints:Teensy_3_6_with_headers | 1 |  | SparkFun Electronics | 1568-DEV-16996-ND | TEENSY 4.1 (HEADERS)
U5 | 3x Analog Switch | https://www.ti.com/lit/ds/scls430k/scls430k.pdf | Custom Footprints:SN74LV4053ADR | 1 |  | Texas Instruments | SN74LV4053ADR | IC SWITCH SPDT X 3 75OHM 16SOIC
U6 | 3x 10-Bit DAC | https://www.ti.com/lit/ds/symlink/dac104s085-q1.pdf | Custom Footprints:DAC084S085CIMMXNOPB | 1 |  | Texas Instruments | DAC104S085QIMMX/NOPB | IC DAC 10BIT V-OUT 10VSSOP
U7 | 3x Level Shifter | https://assets.nexperia.com/documents/data-sheet/NXB0104.pdf | Custom Footprints:TSSOP14_NXB0104_NEX | 1 |  | Nexperia USA Inc. | NXB0104PWJ | IC TRANSLATOR BIDIR 14TSSOP

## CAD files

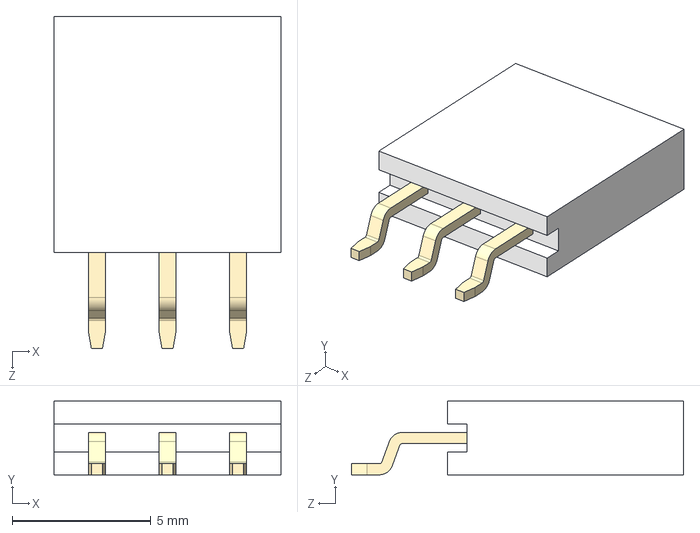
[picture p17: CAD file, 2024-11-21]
KiCAD/LED Cage Plate/CAD models/BG300-03-X-X-A_REVC.step
8.17 x 2.65 x 11.9 mm
body^BG301-xxx
pin^BG301-xxx x 3

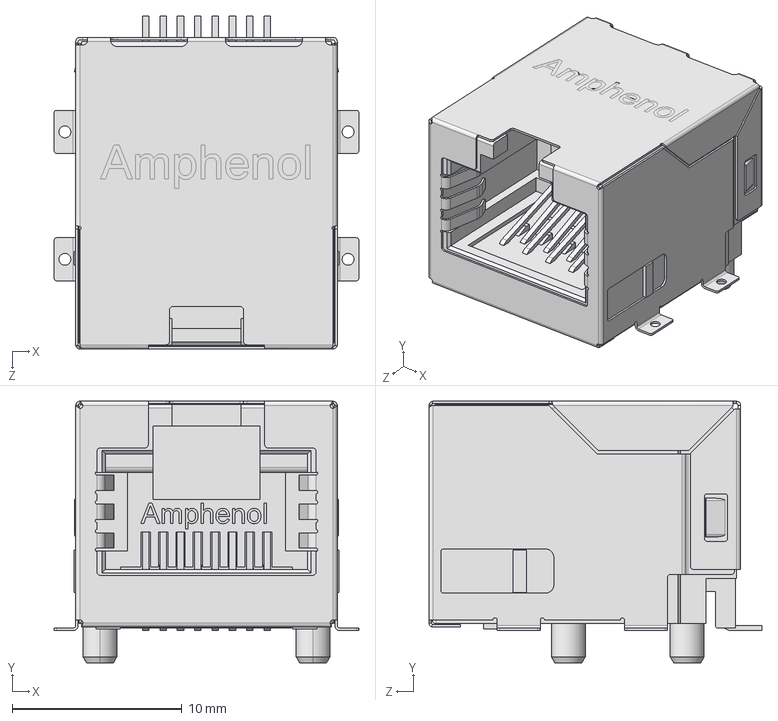
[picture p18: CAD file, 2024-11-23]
KiCAD/LED Controller/CAD models/M-RJE3B-188-6X02-N-REVT1.STEP
17.9 x 15.4 x 19.6 mm

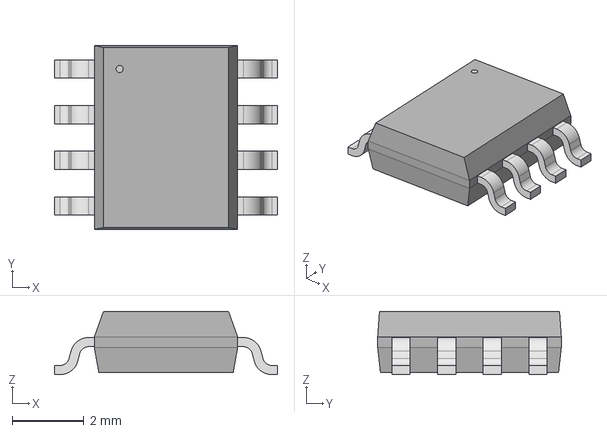
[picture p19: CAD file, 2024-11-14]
KiCAD/LED Cage Plate/CAD models/SO1_SOP-8-A__TPK.step
6.20 x 5.11 x 1.75 mm

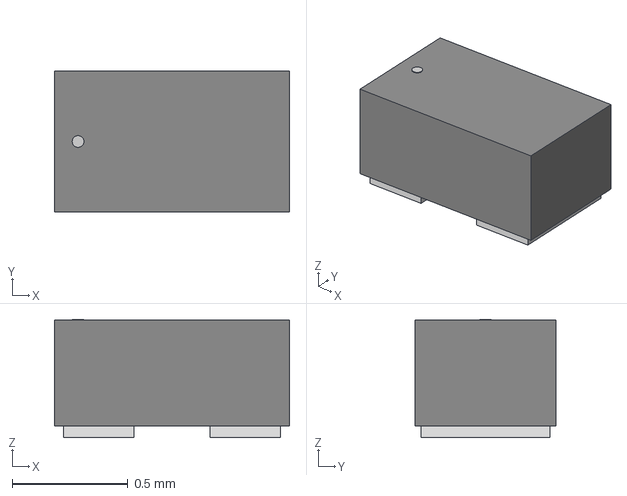
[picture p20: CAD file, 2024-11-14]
KiCAD/LED Cage Plate/CAD models/CR_DFN1006-2_SOD882P-1_NEX.step
1.02 x 0.61 x 0.511 mm

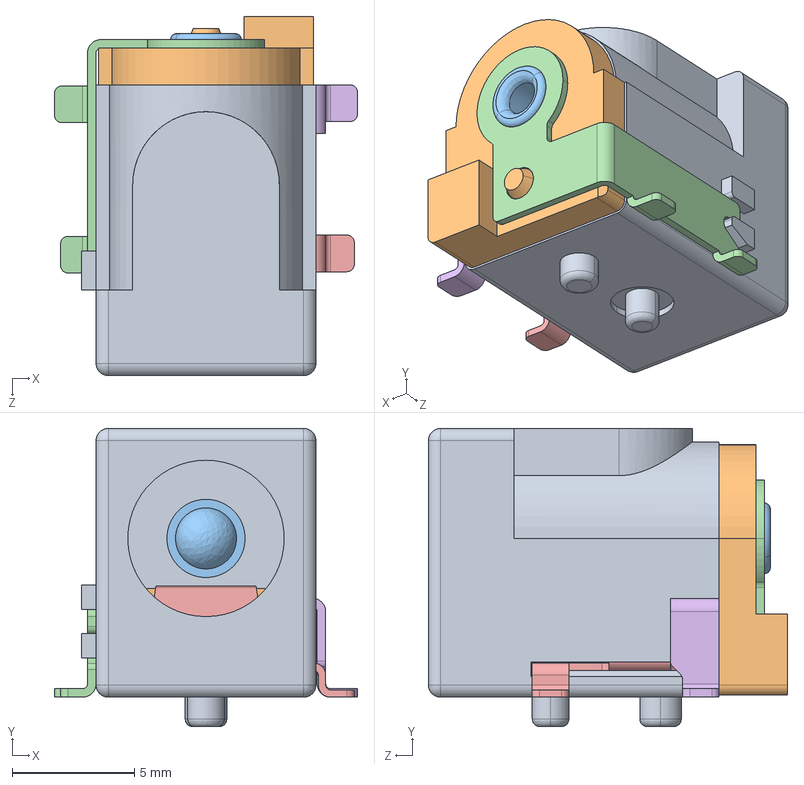
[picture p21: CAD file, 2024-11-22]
KiCAD/LED Controller/CAD models/54-00165.STEP
12.4 x 12.2 x 14.7 mm
54-00165_insulator
54-00165_insulator2
54-00165_center pin
54-00165_center terminal
54-00165_spring terminal
54-00165_switch terminal

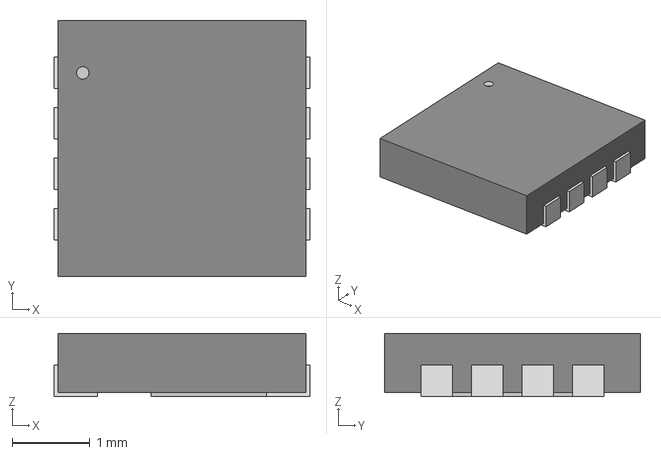
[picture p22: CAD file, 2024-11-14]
KiCAD/LED Cage Plate/CAD models/WDFN8-511DH-O_3p3x3p3x0p65_OSI.step
3.30 x 3.30 x 0.815 mm

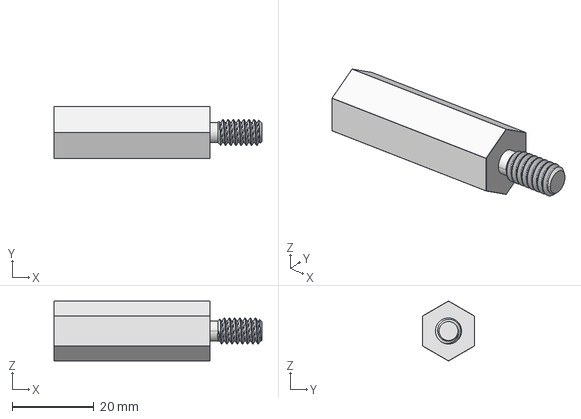
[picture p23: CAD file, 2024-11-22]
KiCAD/LED Controller/CAD models/4689-2520-S-12.stp
50.8 x 12.7 x 14.6 mm

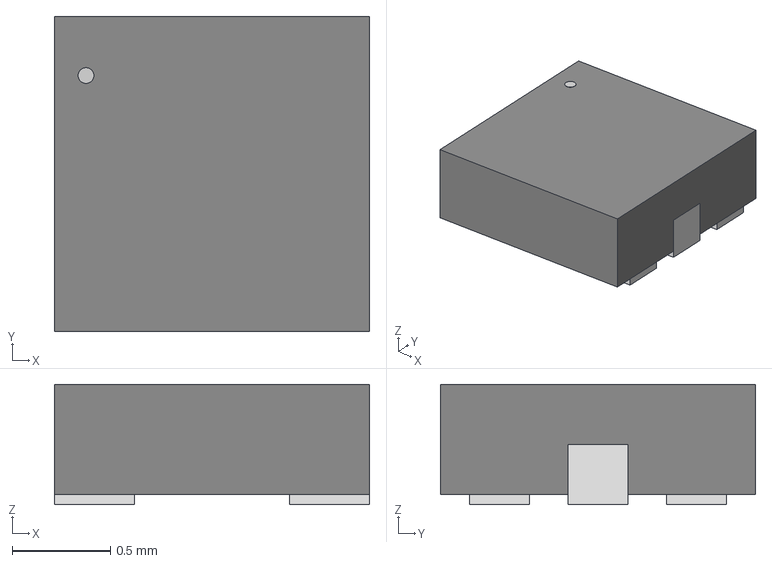
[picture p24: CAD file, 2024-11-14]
KiCAD/LED Cage Plate/CAD models/DFN6_TDS3011_SEM.step
1.60 x 1.60 x 0.612 mm

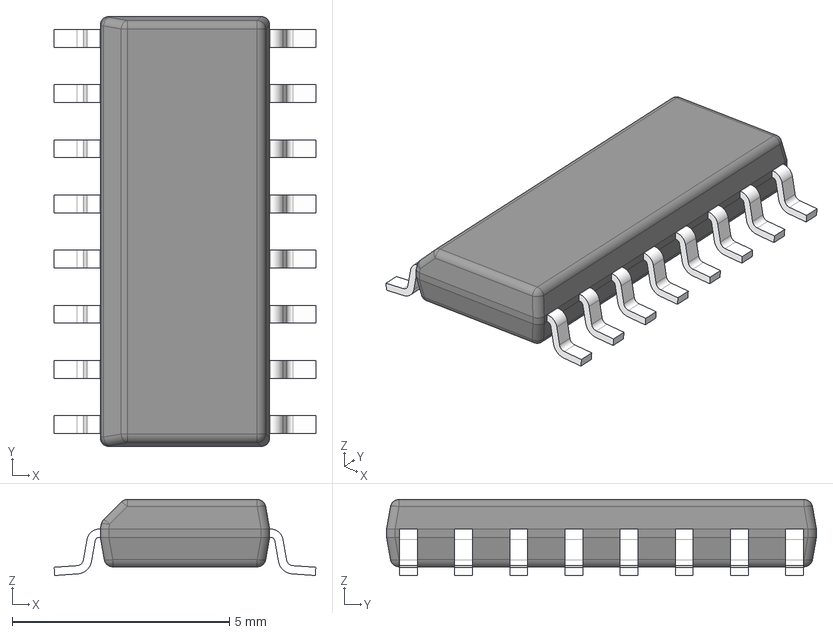
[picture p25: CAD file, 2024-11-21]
KiCAD/LED Controller/CAD models/D0016A.stp
6.03 x 9.90 x 1.75 mm
BODY-SO
LEAD-SO x 16
PIN1-ID

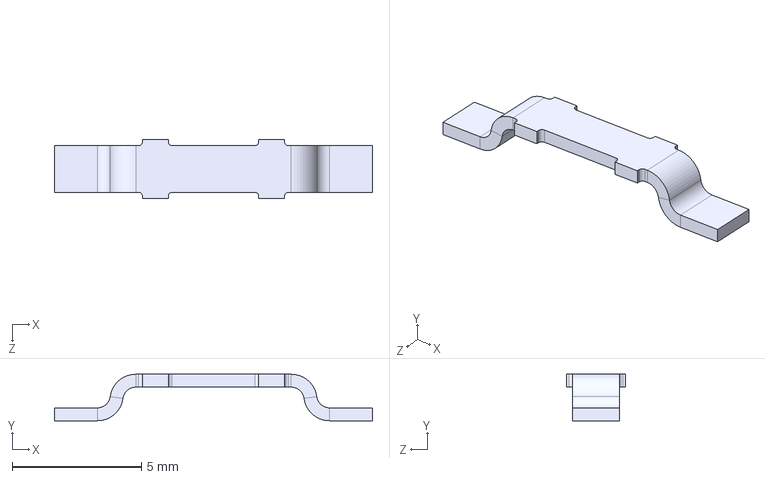
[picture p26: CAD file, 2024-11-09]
KiCAD/LED Cage Plate/CAD models/5104.step
12.3 x 1.80 x 2.30 mm

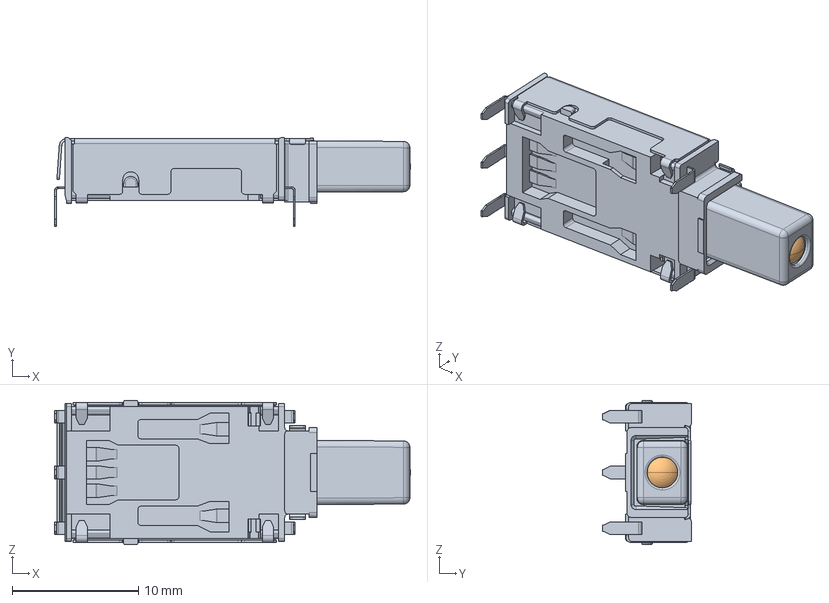
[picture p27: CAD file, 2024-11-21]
KiCAD/LED Controller/CAD models/ELUMOATHQ3C12.stp
28.2 x 7.02 x 11.4 mm

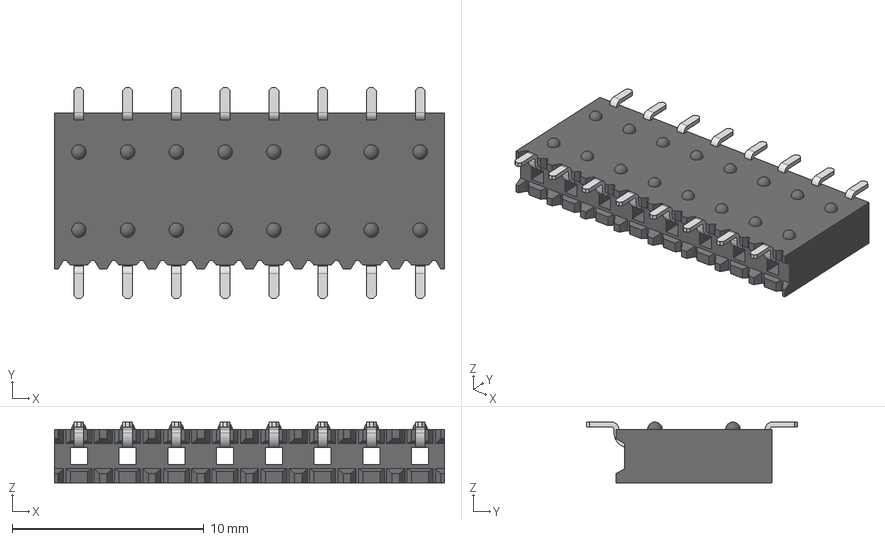
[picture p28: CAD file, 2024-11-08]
KiCAD/LED Cage Plate/CAD models/SSM-108-F-SH-TR.step
20.3 x 11.0 x 3.17 mm
SSM-108-F-SH-TR_body
C-58-06-F8

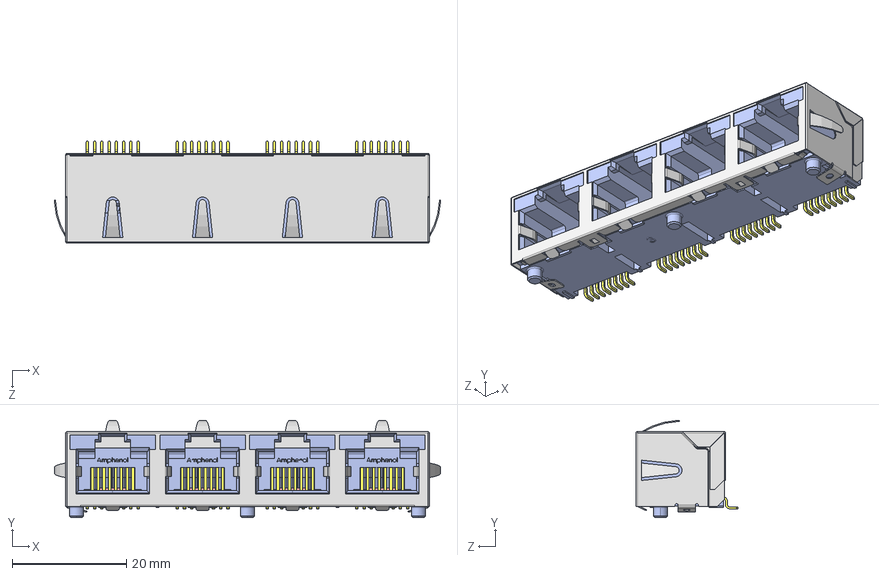
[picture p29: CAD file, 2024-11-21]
KiCAD/LED Controller/CAD models/M-RJSSE-5380-04-REVT1.STEP
67.7 x 17.0 x 17.9 mm

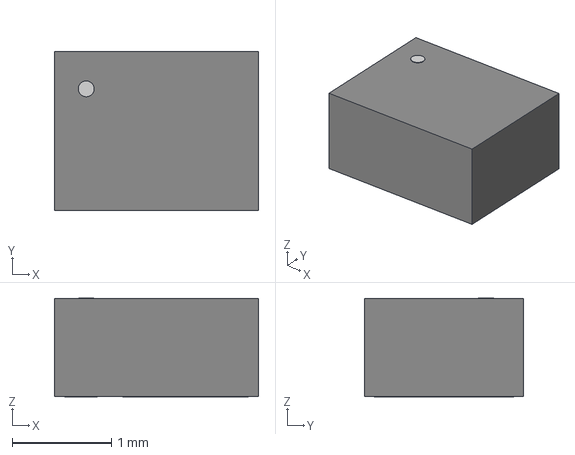
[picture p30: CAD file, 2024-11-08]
KiCAD/LED Cage Plate/CAD models/LED_XLAMP_XE-G_CRW.step
2.06 x 1.60 x 0.997 mm

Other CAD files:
Software/GUI_code/gui_state.obj
KiCAD/LED Controller/CAD models/TSSOP14_NXB0104_NEX.step
KiCAD/LED Cage Plate/CAD models/SN74LVC1G139DCUR.step
KiCAD/LED Cage Plate/CAD models/30 mm Cage Plate LED MCPCB.step
KiCAD/LED Cage Plate/CAD models/CFP5_SOD128_NEX.step
KiCAD/LED Cage Plate/CAD models/IND_3965101_WRE.step
KiCAD/LED Cage Plate/CAD models/LED_SST-20-WxS-A120_LMD.step
KiCAD/LED Cage Plate/CAD models/P-SON4.step
KiCAD/LED Cage Plate/CAD models/SO-8EP_3P9X4P95_DIO.step
KiCAD/LED Cage Plate/CAD models/SRP 1038A series.stp
KiCAD/LED Cage Plate/CAD models/SSM-104-L-SH.step
KiCAD/LED Cage Plate/CAD models/SSM-106-F-SH-TR.step
KiCAD/LED Cage Plate/CAD models/SST-10-IRD-B90H-S810.step
KiCAD/LED Cage Plate/CAD models/Thorlabs 30 mm Cage Plate LED MCPCB.step
KiCAD/LED Cage Plate/CAD models/cage plate set.FCStd
KiCAD/LED Cage Plate/Thorlabs 30 mm Cage Plate LED MCPCB.step
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

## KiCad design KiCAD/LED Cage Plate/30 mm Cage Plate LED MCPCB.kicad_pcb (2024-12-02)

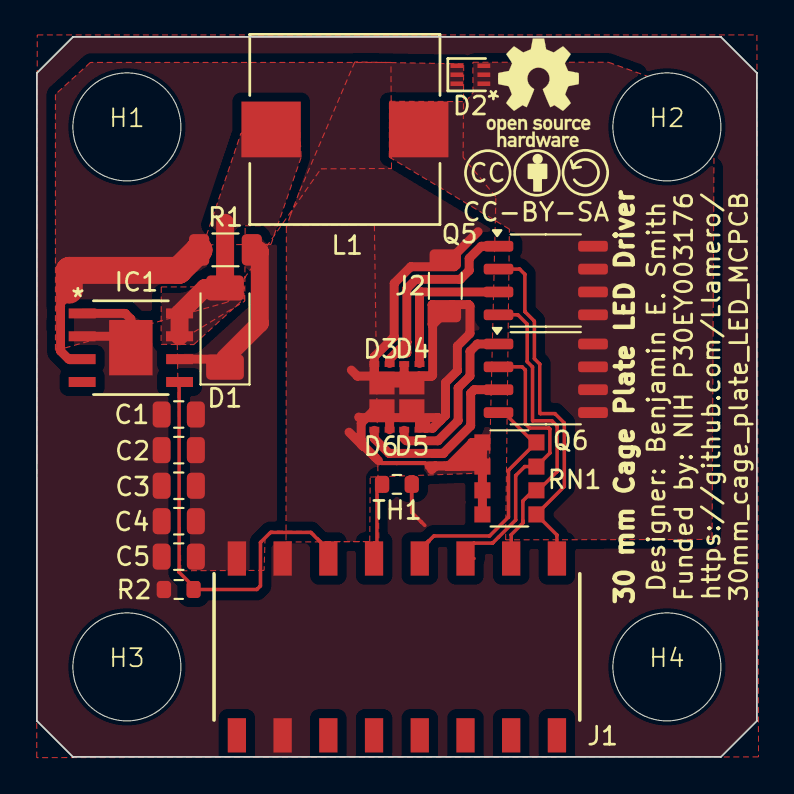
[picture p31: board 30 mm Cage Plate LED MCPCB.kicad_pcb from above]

Board: 2 copper layers, 40.0 x 40.0 mm, 27 parts (0 on the bottom side), 15 nets.

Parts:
C1, C2, C3, C4, C5: 22μF; C_0805_2012Metric
D1: D_Schottky; D_SOD-128
D2: D_Zener; DFN6_TDS3011_SEM
D3, D4, D5, D6: LED_Pad; LED_XLAMP_XE-G_CRW
H1, H2, H3, H4: MountingHole; 6MM NPTH
IC1: AL8843QSP-13; SO-8EP_3P9X4P95_DIO
J1: Conn_01x08_Socket; SAMTEC_SSM-108-F-SH-TR
J2: 0; R_1206_3216Metric
L1: 47μH; SRP1038A-220M_BRN
Q5, Q6: 2x_p-channel; SOP-8_3.9x4.9mm_P1.27mm
R1: 0.040; R_1206_3216Metric
R2: 4700; R_0603_1608Metric
RN1: 4700; R_Array_Convex_4x1206
SYM1: Logo_Open_Hardware_Small; OSHW-Logo_5.7x6mm_SilkScreen
SYM2: Logo_Open_Hardware_Small; CC-BY-SA Symbol
TH1: Thermistor; R_0603_1608Metric

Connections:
/1: J1.8, Q5.2 (G2), RN1.5 (R4.2)
/2: J1.7, Q5.4 (G1), RN1.6 (R3.2)
/3: J1.6, Q6.2 (G2), RN1.7 (R2.2)
/4: J1.5, Q6.4 (G1), RN1.8 (R1.2)
/LED+: D2.1 (K), D3.2 (A), D3.3 (PAD), D4.2 (A), D4.3 (PAD), D5.2 (A), D5.3 (PAD), D6.2 (A), D6.3 (PAD), IC1.3 (SET), J2.1, J2.2, R1.1, RN1.1 (R1.1), RN1.2 (R2.1), RN1.3 (R3.1), RN1.4 (R4.1)
/LED-: D2.2 (A), L1.1, Q5.5 (D1), Q5.6 (D1), Q5.7 (D2), Q5.8 (D2), Q6.5 (D1), Q6.6 (D1), Q6.7 (D2), Q6.8 (D2)
/PWM: IC1.5 (CTRL), J1.3, R2.1
/Temp: J1.4, TH1.2
/Vin: C1.2, C2.2, C3.2, C4.2, C5.2, D1.1 (K), IC1.6 (VIN), J1.1, R1.2
GND: C1.1, C2.1, C3.1, C4.1, C5.1, IC1.1 (GND), IC1.2 (GND), IC1.EPAD, J1.2, R2.2, TH1.1
unnamed: D1.2 (A), IC1.7 (SW), IC1.8 (SW), L1.2
unnamed: D3.1 (K), Q5.1 (S2)
unnamed: D4.1 (K), Q5.3 (S1)
unnamed: D5.1 (K), Q6.1 (S2)
unnamed: D6.1 (K), Q6.3 (S1)

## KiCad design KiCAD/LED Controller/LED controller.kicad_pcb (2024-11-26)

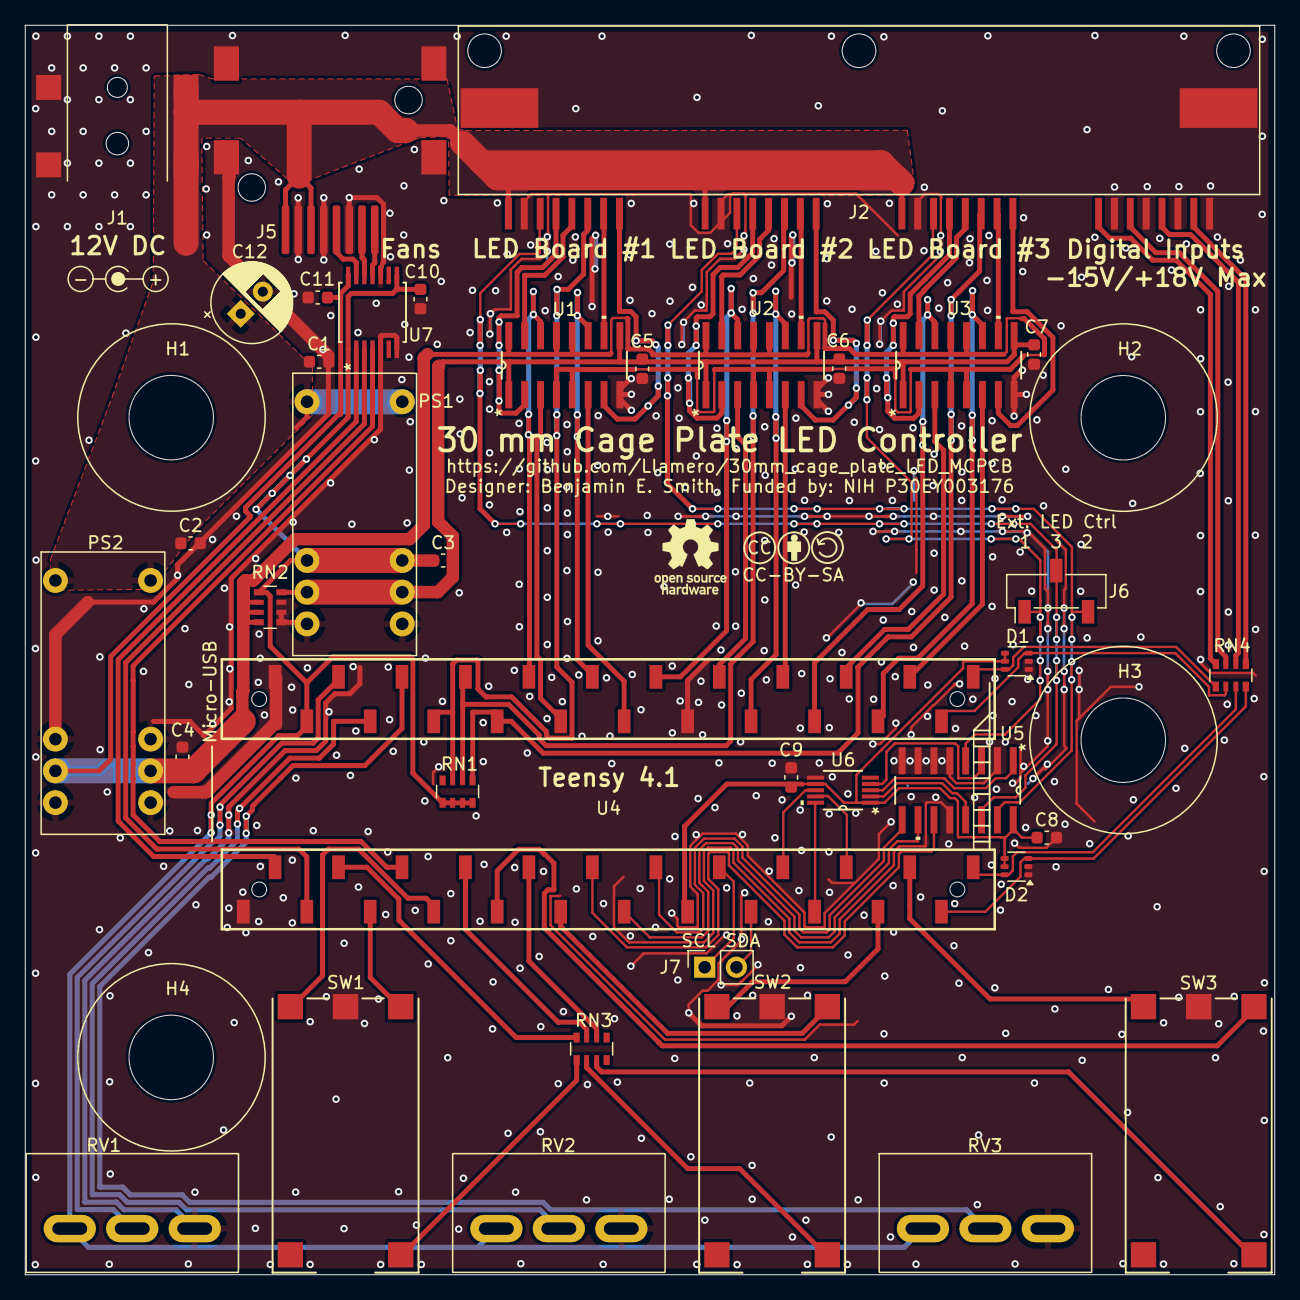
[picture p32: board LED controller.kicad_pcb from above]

Board: 2 copper layers, 100.0 x 100.0 mm, 45 parts (0 on the bottom side), 75 nets.

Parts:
C1, C2, C3, C4, C5, C6, C7, C8, C9, C10, C11: 1µF; C_0603_1608Metric
C12: 220µF; CP_Radial_D6.3mm_P2.50mm
D1, D2: BAT54BRW; SOT-363_SC-70-6
H1, H2, H3, H4: MountingHole; 1-4_20 standoff
J1: Barrel_Jack_Switch; DC-jack_54-00165
J2: 4x RJ45; RJ45_x4-RJSSE-5380-04
J5: 8P8C_Shielded; 1x RJ45
J6: Conn_01x03_Socket; PinSocket_1x03_P2.54mm_Vertical_SMD_Pin1Left
J7: Conn_01x02_Socket; PinSocket_1x02_P2.54mm_Vertical
PS1, PS2: 15V DC-DC; SRS-1215-2
RN1, RN2, RN4: 3600; R_Array_Convex_4x0603
RN3: 390; R_Array_Convex_4x0603
RV1, RV2, RV3: 10k; P160KN2-4QC20B10K
SW1, SW2, SW3: ELUMOASAQ2C22; ELUMOASAQ2C22_CNK
SYM1: Logo_Open_Hardware_Small; CC-BY-SA Symbol
SYM2: Logo_Open_Hardware_Small; OSHW-Logo_5.7x6mm_SilkScreen
SYM3: Logo_Center_Positive; Polarity
U1, U2, U3: 4x Gate Driver; D16-4x gate driver
U4: Teensy4.1; Teensy_3_6_with_headers
U5: 3x Analog Switch; SN74LV4053ADR
U6: 3x 10-Bit DAC; DAC084S085CIMMXNOPB
U7: 3x Level Shifter; TSSOP14_NXB0104_NEX

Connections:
/1-1: J2.5, U1.15 (4Y)
/1-2: J2.4, U1.2 (1Y)
/1-3: J2.7, U1.10 (3Y)
/1-4: J2.8, U1.7 (2Y)
/2-1: J2.13, U2.15 (4Y)
/2-2: J2.12, U2.2 (1Y)
/2-3: J2.15, U2.10 (3Y)
/2-4: J2.16, U2.7 (2Y)
/3-1: J2.21, U3.15 (4Y)
/3-2: J2.20, U3.2 (1Y)
/3-3: J2.23, U3.10 (3Y)
/3-4: J2.24, U3.7 (2Y)
/3v3: C3.1, C8.1, C9.1, C10.1, D1.4, D1.5, D2.4, D2.5, PS1.6 (-Vout), PS1.11, RN1.1 (R1.1), RN1.2 (R2.1), RN1.3 (R3.1), RN1.4 (R4.1), RN2.1 (R1.1), RV1.1, RV2.1, RV3.1, U4.15 (3V3), U4.46 (3V3), U5.16 (VCC), U6.1 (VA), U6.7 (VREFIN), U7.1 (VCC(A)), U7.8 (OE)
/5V: C4.2, C11.1, PS2.7 (+Vout), PS2.10, RN2.2 (R2.1), RN2.3 (R3.1), RN2.4 (R4.1), U1.4 (1E1), U1.5 (1E2), U1.12 (2E1), U1.13 (2E2), U1.16 (VCC1), U2.4 (1E1), U2.5 (1E2), U2.12 (2E1), U2.13 (2E2), U2.16 (VCC1), U3.4 (1E1), U3.5 (1E2), U3.12 (2E1), U3.13 (2E2), U3.16 (VCC1), U4.48 (VIN), U7.14 (VCC(B))
/12V: C1.1, C2.1, C12.1, J1.1, J2.1, J2.9, J2.17, J5.1, J5.3, PS1.1 (+Vin), PS1.16, PS2.1 (+Vin), PS2.16
/18V: C3.2, C5.1, C6.1, C7.1, PS1.7 (+Vout), PS1.10, RN2.8 (R1.2), U1.1 (VCC2), U1.9 (VCC3), U2.1 (VCC2), U2.9 (VCC3), U3.1 (VCC2), U3.9 (VCC3)
/A-D_input_1: D1.6, RN4.1 (R1.1), U4.25 (33_MCLK2)
/A-D_input_2: D1.3, RN4.2 (R2.1), U4.26 (34_RX8)
/A-D_input_3: D2.6, RN4.3 (R3.1), U4.24 (32_OUT1B)
/A-D_input_4: D2.3, RN4.4 (R4.1), U4.23 (31_CTX3)
/Ana1: U5.13 (1Y1), U6.2 (VOUTA)
/Ana2: U5.1 (2Y1), U6.3 (VOUTB)
/Ana3: U5.3 (3Y1), U6.4 (VOUTC)
/CS: U4.20 (28_RX7), U6.9 (~SYNC)
/Ch1a: U1.14 (4A), U4.39 (17_A3_TX4_SDA1)
/Ch1b: U1.3 (1A), U4.38 (16_A2_RX4_SCL1)
/Ch1c: U1.11 (3A), U4.37 (15_A1_RX3_SPDIF_IN)
/Ch1d: U1.6 (2A), U4.36 (14_A0_TX3_SPDIF_OUT)
/Ch2a: U2.14 (4A), U4.35 (13_SCK_LED)
/Ch2b: U2.3 (1A), U4.33 (41_A17)
/Ch2c: U2.11 (3A), U4.32 (40_A16)
/Ch2d: U2.6 (2A), U4.31 (39_MISO1_OUT1A)
/Ch3a: U3.14 (4A), U4.30 (38_CS1_IN1)
/Ch3b: U3.3 (1A), U4.29 (37_CS)
/Ch3c: U3.11 (3A), U4.28 (36_CS)
/Ch3d: U3.6 (2A), U4.27 (35_TX8)
/Ctrl1: J2.3, J6.2, U5.14 (1-COM)
/Ctrl2: J2.11, J6.3, U5.15 (2-COM)
/Ctrl3: J2.19, J6.1, U5.4 (3-COM)
/Fan_PWM1: J5.5, U7.13 (B1)
/Fan_PWM1_low: U4.2 (0_RX1_CRX2_CS1), U7.2 (A1)
/Fan_PWM2: J5.7, U7.12 (B2)
/Fan_PWM2_low: U4.3 (1_TX1_CTX2_MISO1), U7.3 (A2)
/Fan_PWM3: J5.8, U7.11 (B3)
/Fan_PWM3_low: U4.6 (4_BCLK2), U7.4 (A3)
/LED_PWM1: U4.12 (10_CS_MQSR), U5.11 (A)
/LED_PWM2: U4.13 (11_MOSI_CTX1), U5.10 (B)
/LED_PWM3: U4.14 (12_MISO_MQSL), U5.9 (C)
/MOSI: U4.18 (26_A12_MOSI1), U6.8 (DIN)
/Pot1: RV1.2, U4.45 (23_A9_CRX1_MCLK1)
/Pot2: RV2.2, U4.44 (22_A8_CTX1)
/Pot3: RV3.2, U4.43 (21_A7_RX5_BCLK1)
/SCK: U4.19 (27_A13_SCK1), U6.10 (SCLK)
/SCL: J7.1, U4.16 (24_A10_TX6_SCL2)
/SDA: J7.2, U4.17 (25_A11_RX6_SDA2)
/SW1: SW1.3, U4.7 (5_IN2)
/SW1 green: SW1.1, U4.5 (3_LRCLK2)
/SW1 red: RN3.4 (R4.1), U4.4 (2_OUT2)
/SW2: SW2.3, U4.21 (29_TX7)
/SW2 green: SW2.1, U4.11 (9_OUT1C)
/SW2 red: RN3.3 (R3.1), U4.8 (6_OUT1D)
/SW3: SW3.3, U4.22 (30_CRX3)
/SW3 green: SW3.1, U4.9 (7_RX2_OUT1A)
/SW3 red: RN3.2 (R2.1), U4.10 (8_TX2_IN1)
/Temp1: J2.6, RN1.7 (R2.2), U4.42 (20_A6_TX5_LRCLK1)
/Temp2: J2.14, RN1.6 (R3.2), U4.41 (19_A5_SCL)
/Temp3: J2.22, RN1.5 (R4.2), U4.40 (18_A4_SDA)
/in1: J2.25, RN4.8 (R1.2)
/in2: J2.27, RN4.7 (R2.2)
/in3: J2.29, RN4.6 (R3.2)
/in4: J2.31, RN4.5 (R4.2)
GND: C1.2, C2.2, C4.1, C5.2, C6.2, C7.2, C8.2, C9.2, C10.2, C11.2, C12.2, D1.1, D1.2, D2.1, D2.2, J1.2, J1.3, J2.2, J2.10, J2.18, J2.26, J2.28, J2.30, J2.32, J2.SH, J5.2, J5.4, J5.6, J5.SH, PS1.8 (-Vin), PS1.9, PS2.6 (-Vout), PS2.8 (-Vin), PS2.9, PS2.11, RN2.5 (R4.2), RN2.6 (R3.2), RN2.7 (R2.2), RV1.3, RV2.3, RV3.3, SW1.2, SW2.2, SW3.2, U1.8 (GND), U2.8 (GND), U3.8 (GND), U4.1 (GND), U4.34 (GND), U4.47 (GND), U5.2 (2Y0), U5.5 (3Y0), U5.6 (INH), U5.7 (GND), U5.8 (GND), U5.12 (1Y0), U6.6 (GND), U7.5 (A4), U7.7 (GND), U7.10 (B4)
unnamed: RN3.7 (R2.2), SW3.5
unnamed: RN3.6 (R3.2), SW2.5
unnamed: RN3.5 (R4.2), SW1.5

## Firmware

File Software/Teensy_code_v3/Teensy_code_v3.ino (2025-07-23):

#include <SPI.h>
#include "pinSetup.h"
#include "DAC.h"
#include "PacketSerial.h"
#include "SDcard.h"
#include <EEPROM.h>
#include <TimeLib.h> //Set RTC time and get time strings
#include <eFlexPwm.h>

//////////////STRUCT//////////////STRUCT//////////////STRUCT//////////////STRUCT//////////////STRUCT//////////////STRUCT//////////////STRUCT//////////////STRUCT//////////////STRUCT//////////////STRUCT//////////////STRUCT//////////////STRUCT

#pragma pack(1) //Remove alignment padding bytes in structs - https://forum.pjrc.com/threads/50536-problem-with-union-in-Teensy-3-5
const uint8_t N_BOARDS = 3; //Number of boards connected to the LED driver
const uint8_t N_LEDS = 4; //Number of LEDs per board

struct configurationStruct{ //259 bytes
  uint8_t prefix;
  char driver_name[16]; //Name of LED driver: "default name"
  char led_names[3][4][16]; //Name of each LED channel
  boolean led_active[3][4]; //Whether LED channel is in use: {false, false, false, false}
  uint16_t current_limit[3][4]; //Current limit for each channel on DAC values: {0,0,0,0}
  boolean simul_led; //Whether LED boards can be turned on simultaneously
  uint16_t warn_temp; //Warn temp for three LED boards respectively in ADC units: {0,0,0}
  uint16_t fault_temp; //Fault temp for transistor, resistor, and external respectively in ADC units: {0,0,0}
  uint16_t driver_fan[2]; //Driver fan min and max temperatures in ADC units: {65535, 65535}
  uint8_t audio_volume[2]; //Status and alarm volumes for transducer: {10, 100}
  bool pushbutton_intensity; //LED intensity - on/off
  uint8_t pushbutton_mode; //LED illumination mode when alarm is active
  uint8_t checksum; //Checksum to confirm that configuration is valid
};

const struct defaultConfigurationStruct{ //259 bytes
  uint8_t prefix = 2;
  char driver_name[16] = "Unnamed driver "; //Name of LED driver: "default name"
  char led_names[3][4][16] = {{"LED #1         ", "LED #2         ", "LED #3         ", "LED #4         "}, //Name of each LED channel
                              {"LED #5         ", "LED #6         ", "LED #7         ", "LED #8         "},
                              {"LED #9         ", "LED #10        ", "LED #11        ", "LED #12        "}};
  boolean led_active[3][4] = {{false, false, false, false}, //Whether LED channel is in use: {false, false, false, false}
                              {false, false, false, false},
                              {false, false, false, false}};
  uint16_t current_limit[3][4] = {{65535,65535,65535,65535}, //Current limit for each channel on DAC values: {0,0,0,0}
                                  {65535,65535,65535,65535},
                                  {65535,65535,65535,65535}};
  boolean simul_led = false; //Whether LED boards can be turned on simultaneously
  uint16_t warn_temp = 14604; //Warn at 60°C
  uint16_t fault_temp = 8891; //Fault at 80°C
  uint16_t driver_fan[2] = {33963, 27958}; //Fan on at 30°C, fan max at 40°C
  uint8_t audio_volume[2] = {2, 100}; //Status and alarm volumes for transducer: {10, 100}
  bool pushbutton_intensity = true; //LED intensity at full intensity
  uint8_t pushbutton_mode = 1; //LED illumination mode when alarm is active
  uint8_t checksum = 227; //Checksum to confirm that configuration is valid
} defaultConfig;

struct syncStruct{ //158 bytes
  uint8_t prefix;
  uint8_t mode; //Type of sync - digital, analog, confocal, etc.
  
  uint8_t digital_channel; //The input channel for the sync signal
  uint8_t digital_mode[2]; //The digital sync mode  in the LOW and HIGH trigger states respectively
  uint8_t digital_led[2]; //The active LED channel in the LOW and HIGH trigger states respectively
  uint16_t digital_pwm[2]; //The PWM value in the LOW and HIGH trigger states respectively
  uint16_t digital_current[2]; //The DAC value in the LOW and HIGH trigger states respectively
  uint32_t digital_duration[2]; //The maximum number of milliseconds to hold LED state

  uint8_t analog_led[3]; //The active LED channel for each board

  boolean shutter_polarity; //Shutter polarity when scan is active
  uint8_t confocal_channel; //The input channel for the line sync signal
  boolean confocal_sync_mode; //Whether the line sync is digital (true) or analog (false)
  boolean confocal_sync_polarity[2]; //Sync polarity for digital and analog sync inputs
  uint16_t confocal_threshold; //Threshold for analog sync trigger
  boolean confocal_scan_mode; //Whether scan is unidirectional (true) or bidrectional (false)
  uint32_t confocal_mirror_period; //Time in clock cycles for the scanning mirror to complete one cycle
  uint32_t confocal_delay[3]; //Delay in clock cycles for each sync delay

  uint8_t confocal_mode[2]; //The digital sync mode  in the image and flyback states respectively
  uint8_t confocal_led[2]; //The active LED channel in the image and flyback states respectively
  uint16_t confocal_pwm[2]; //The PWM value in the image and flyback states respectively
  uint16_t confocal_current[2]; //The DAC value in the image and flyback states respectively
  uint32_t confocal_duration[2]; //The maximum number of milliseconds to hold LED state

  uint8_t checksum; //Checksum to confirm that configuration is valid
};

const struct defaultSyncStruct{ //158 bytes
  uint8_t prefix = 4;
  uint8_t mode = 0; //Type of sync - digital, analog, confocal, etc.
  
  uint8_t digital_channel = 0; //The input channel for the sync signal
  uint8_t digital_mode[2] = {0,0}; //The digital sync mode  in the LOW and HIGH trigger states respectively
  uint8_t digital_led[2] = {0,0}; //The active LED channel in the LOW and HIGH trigger states respectively
  uint16_t digital_pwm[2] = {0,0}; //The PWM value in the LOW and HIGH trigger states respectively
  uint16_t digital_current[2] = {0,0}; //The DAC value in the LOW and HIGH trigger states respectively
  uint32_t digital_duration[2] = {0,0}; //The maximum number of milliseconds to hold LED state
  
  uint8_t analog_led[3] = {0, 0, 0}; //The active LED channel for each board

  boolean shutter_polarity = true; //Shutter polarity when scan is active
  uint8_t confocal_channel = 0; //The input channel for the line sync signal
  boolean confocal_sync_mode = false; //Whether the line sync is digital (false) or analog (true)
  boolean confocal_sync_polarity[2] = {true, true}; //Sync polarity for digital and analog sync inputs
  uint16_t confocal_threshold = 2000; //Threshold for analog sync trigger
  boolean confocal_scan_mode = true; //Whether scan is unidirectional (false) or bidrectional (true)
  uint32_t confocal_mirror_period = 600000; //Time in µs for the scanning mirror to complete one cycle
  uint32_t confocal_delay[3] = {0,36000,0}; //Delay in clock cycles for each sync delay
  
  uint8_t confocal_mode[2] = {0,0}; //The digital sync mode  in the image and flyback states respectively
  uint8_t confocal_led[2] = {0,0}; //The active LED channel in the image and flyback states respectively
  uint16_t confocal_pwm[2] = {0,0}; //The PWM value (in clock cycles) in the image and flyback states respectively
  uint16_t confocal_current[2] = {0,0}; //The DAC value in the image and flyback states respectively
  uint32_t confocal_duration[2] = {0,0}; //The maximum number of milliseconds to hold LED state

  uint8_t checksum = 20; //Checksum to confirm that configuration is valid
} defaultSync;

struct sequenceHeaderStruct{ //6 bytes
  uint8_t prefix;
  uint8_t file_index;
  uint32_t buffer_size;
};

struct sequenceStruct{ //9 bytes
  uint8_t led_id; //LED channel
  uint16_t led_pwm; //LED PWM (analog out units)
  uint16_t led_current; //LED current (DAC units)
  uint32_t led_duration; //LED duration (microseconds)
};

struct statusStruct{
  uint8_t led_channel[3]; //Active LED channel
  uint16_t led_pwm[3]; //PWM value for internal and external fan respectively
  uint16_t led_current[3]; //DAC value for active LED
  uint8_t mode; //0=Sync, 1=PWM, 2=Current, 3=Off
  boolean state; //0=Standby (confocal), LOW (digital), etc. 1 = Scanning (confocal), HIGH (digital), etc.
  boolean driver_control; //True = driver controls itself, False = GUI controls driver
  uint16_t temp[3]; //ADC temp reading of mosfet, resistor, and external respectively
  uint16_t fan_speed[3]; //PWM value for internal and external fan respectively
};

const struct defaultStatusStruct{
  uint8_t led_channel[3] = {N_LEDS, N_LEDS, N_LEDS}; //Set active LED channel to off
  uint16_t led_pwm[3] = {0, 0, 0}; //PWM value for internal and external fan respectively
  uint16_t led_current[3] = {0, 0, 0}; //DAC value for active LED
  uint8_t mode = 3; //0=Sync, 1=PWM, 2=Current, 3=Off
  boolean state = 0; //0=Standby (confocal), LOW (digital), etc. 1 = Scanning (confocal), HIGH (digital), etc.
  boolean driver_control = true; //True = driver controls itself, False = GUI controls driver
  uint16_t temp[3] = {defaultConfig.driver_fan[0], defaultConfig.driver_fan[0], defaultConfig.driver_fan[0]}; //ADC temp reading of mosfet, resistor, and external respectively
  uint16_t fan_speed[3] = {0, 0, 0}; //PWM value for internal and external fan respectively
} defaultStatus;

const struct prefixStruct{
  uint8_t message = 0; //Send error, warning, and notification messages to be diplayed as pop-up in GUI
  uint8_t connection = 1; //Recv magic number at connection start and confirm with magic reply
  uint8_t send_config = 2; //Send active configuration byte file
  uint8_t recv_config = 3; //Recv and apply new configuration byte file
  uint8_t send_sync = 4; //Send active configuration byte file
  uint8_t recv_sync = 5; //Recv and apply new configuration byte file
  uint8_t send_seq = 6; //Send specified seq byte file from SD card if available
  uint8_t recv_seq = 7; //Recv specified seq byte file and save on SD card if available
  uint8_t send_id = 8; //Send the driver ID only
  uint8_t recv_time = 9; //Receive the unix time of the GUI to sync driver RTC
  uint8_t recv_stream = 10; //Signal the driver is ready to receive stream that is queued
  uint8_t send_stream = 11; //If recv - signals that ready for next packet
  uint8_t status_update = 12; //Status update packet for driver or GUI
  uint8_t calibration = 13; //Send a plot of LED square wave test output for calibrating op-amp compensation trimpots
  uint8_t gui_disconnect = 14; //GUI is disconnecting form LED driver
  uint8_t measure_period = 15; //Measure the mirror period - return as 
  uint8_t test_current = 16; //Measure the output for each channel - return as 4x uint16_t - disable channels with output below 51633 (0.7 V diff) to protect opamp.
  uint8_t test_volume = 17; //Test status or indicator volume
  uint8_t long_off = 148; //Prefix sent when computer has been off for a while
} prefix;

//////////////UNION//////////////UNION//////////////UNION//////////////UNION//////////////UNION//////////////UNION//////////////UNION//////////////UNION//////////////UNION//////////////UNION//////////////UNION//////////////UNION//////////////UNION

//Convert between byte list and float
union FLOATUNION
{
 float float_var;
 uint8_t bytes[4];
}floatUnion;

//Convert between byte list and int
union INTUNION
{
 int int_var;
 uint8_t bytes[4];
}intUnion;

//Convert between byte list and int
union BYTE16UNION
{
 uint16_t bytes_var;
 uint8_t bytes[2];
}uint16Union;

union BYTE32UNION
{
 uint32_t bytes_var;
 uint8_t bytes[4];
}uint32Union;

//From: https://forum.arduino.cc/index.php?topic=263107.0
union CONFIGUNION //Convert binary buffer <-> config setup
{
   configurationStruct c;
   byte byte_buffer[sizeof(defaultConfigurationStruct)];
} conf;

union SYNCUNION //Convert binary buffer <-> sync setup
{
   syncStruct s;
   byte byte_buffer[sizeof(defaultSyncStruct)];
} sync;

union SEQHEADERUNION //Convert binary buffer <-> sync setup
{
   sequenceHeaderStruct s;
   byte byte_buffer[sizeof(sequenceHeaderStruct)];
} seq_header;

union SEQUNION //Convert binary buffer <-> sync setup
{
   sequenceStruct s;
   byte byte_buffer[sizeof(sequenceStruct)];
}seq;
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

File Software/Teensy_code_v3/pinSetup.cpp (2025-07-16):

/*
  Default configuration of teensy pins
*/

#include "Arduino.h"
#include "pinSetup.h"
#include "ADC.h"
#include "ADC_util.h"
#include "Wire.h"
#include "eFlexPwm.h"

ADC *adc = new ADC(); // adc object;

// avoid systematically prefixing objects with the namespace
using namespace eFlex;

// My eFlexPWM submodules (Hardware > PWM2: SM[0], SM[2], SM[3])
SubModule Sm13 (8, 7);
SubModule Sm22 (6, 9);
SubModule Sm42 (2, 3);
Timer &Tm1 = Sm13.timer();
Timer &Tm2 = Sm22.timer();
Timer &Tm4 = Sm42.timer();

uint8_t dutyCyclePercent = 0;

//NOTE: It seems that in this compiler lists longer than 4 need to be built in CPP while shorter lists need to be built in header with constexpr
const int pinSetup::RELAY[][4] = {{14, 15, 16, 17}, {39, 40, 41, 13}, {35, 36, 37, 38}}; //SSR relays for changing LED channel
const int pinSetup::INTERLINE[] = {10, 11, 12}; //Switch between analog input and gnd to turn off LED
const int pinSetup::ALARM[] = {24, 25}; //Audible alarm
const int pinSetup::BOARD_TEMP[] = {20, 19, 18}; //NTC thermistor monitoring LED board temperature(s)
const int pinSetup::FAN_PWM[] = {0, 4, 5}; //5V PWM to control internal fan speed
const int pinSetup::PUSHBUTTON[] = {1, 29, 30}; //Four pushbutton inputs 
const int pinSetup::LED[][2] = {{2, 3}, {6, 9}, {8, 7}}; //Indicator LEDs on pushbuttons - red then green
const int pinSetup::POT[] = {23, 22, 21}; //Input voltage from potentiometer
const int pinSetup::INPUTS[] = {33, 34, 32, 31}; //4-channel analog/digital inputs
//const uint8_t pinSetup::color_list[] = {0, 13, 50, 100}; //4 color settings for pushbutton
const uint8_t pinSetup::color_list[] = {0, 60, 90, 100}; //4 color settings for pushbutton

pinSetup::pinSetup()
{
}

void pinSetup::init(){
}


void pinSetup::configurePins(){
  unsigned int a; //Loop counter
  unsigned int b; //Loop counter
  analogWriteResolution(16);
  
  ///// ADC0 ////
  // reference can be ADC_REFERENCE::REF_3V3, ADC_REFERENCE::REF_1V2 (not for Teensy LC) or ADC_REFERENCE::REF_EXT.
  adc->adc0->setReference(ADC_REFERENCE::REF_3V3); // change all 3.3 to 1.2 if you change the reference to 1V2
  adc->adc0->setAveraging(adc_averaging); // set number of averages
  adc->adc0->setResolution(adc_resolution); // set bits of resolution

  // it can be any of the ADC_CONVERSION_SPEED enum: VERY_LOW_SPEED, LOW_SPEED, MED_SPEED, HIGH_SPEED_16BITS, HIGH_SPEED or VERY_HIGH_SPEED
  // see the documentation for more information
  // additionally the conversion speed can also be ADACK_2_4, ADACK_4_0, ADACK_5_2 and ADACK_6_2,
  // where the numbers are the frequency of the ADC clock in MHz and are independent on the bus speed.
  adc->adc0->setConversionSpeed(ADC_CONVERSION_SPEED::LOW_SPEED); // change the conversion speed
  // it can be any of the ADC_MED_SPEED enum: VERY_LOW_SPEED, LOW_SPEED, MED_SPEED, HIGH_SPEED or VERY_HIGH_SPEED
  adc->adc0->setSamplingSpeed(ADC_SAMPLING_SPEED::LOW_SPEED); // change the sampling speed
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

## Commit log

2023-11-01 Add core components to schematic
    [SO-8EP_3P9X4P95_DIO.step, Thorlabs 30 mm Cage Plate LED MCPCB.kicad_pcb, Thorlabs 30 mm Cage Plate LED MCPCB.kicad_sch, Thorlabs 30 mm Cage Plate LED MCPCB.step]
2023-11-02 Rats nest connected
    [CFP5_SOD128_NEX.step, IND_3965101_WRE.step, LED_SST-20-WxS-A120_LMD.step, SRP 1038A series.stp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]
2023-11-03 Full working draft
    [Thorlabs 30 mm Cage Plate LED MCPCB.kicad_pcb, Thorlabs 30 mm Cage Plate LED MCPCB.kicad_sch]
2023-11-03 PCB optimization
    [Thorlabs 30 mm Cage Plate LED MCPCB.kicad_pcb, Thorlabs 30 mm Cage Plate LED MCPCB.kicad_sch]
2023-11-03 Gerber files added
    [Thorlabs 30 mm Cage Plate LED MCPCB-B_Cu.gbl, Thorlabs 30 mm Cage Plate LED MCPCB-B_Mask.gbs, Thorlabs 30 mm Cage Plate LED MCPCB-B_Paste.gbp, Thorlabs 30 mm C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]
2023-11-03 Add CAD model of setup
    [Thorlabs 30 mm Cage Plate LED MCPCB.step, cage plate set.FCStd]
2023-11-29 Add heatsink
    [30 mm Cage Plate LED MCPCB-B_Cu.gbl, 30 mm Cage Plate LED MCPCB-B_Mask.gbs, 30 mm Cage Plate LED MCPCB-B_Paste.gbp, 30 mm Cage Plate LED MCPCB-B_Silkscreen.gbo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]
2023-11-29 Update naming
    [Thorlabs 30 mm Cage Plate LED MCPCB.step]
2023-12-21 Update README.md
    Add assembly info
2024-01-12 Move PWM and Vin pins apart to prevent fatal shorts of Vin to Ctrl
    [30 mm Cage Plate LED MCPCB.kicad_pcb, 30 mm Cage Plate LED MCPCB.kicad_sch]
2024-11-08 working draft
    [30 mm Cage Plate LED MCPCB.kicad_pcb, LED_XLAMP_XE-G_CRW.step, P-SON4.step, SN74LVC1G139DCUR.step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]
2024-11-09 Before adding mux to PCB
    [30 mm Cage Plate LED MCPCB.kicad_pcb, 30 mm Cage Plate LED MCPCB.kicad_sch, 5104.step]
2024-11-09 Fan added
    [30 mm Cage Plate LED MCPCB.kicad_pcb, 30 mm Cage Plate LED MCPCB.kicad_sch]
2024-11-09 Add logo
    [30 mm Cage Plate LED MCPCB.kicad_pcb]
2024-11-09 Update LICENSE
    Add CC license for PCB
2024-11-09 Add OSHW logo
    [30 mm Cage Plate LED MCPCB.kicad_pcb]
2024-11-09 More copper for LEDs, OSHW logo
    [30 mm Cage Plate LED MCPCB.kicad_pcb, 30 mm Cage Plate LED MCPCB.kicad_sch]
2024-11-14 Add pmos array mux
    [30 mm Cage Plate LED MCPCB.kicad_pcb, 30 mm Cage Plate LED MCPCB.kicad_sch, CR_DFN1006-2_SOD882P-1_NEX.step, DFN6_TDS3011_SEM.step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]
2024-11-15 pmos mux connected - better conduction path
    [30 mm Cage Plate LED MCPCB.kicad_pcb, 30 mm Cage Plate LED MCPCB.kicad_sch]
2024-11-16 Start on driver board
    [30 mm Cage Plate LED MCPCB-B_Cu.gbl, 30 mm Cage Plate LED MCPCB-B_Mask.gbs, 30 mm Cage Plate LED MCPCB-B_Paste.gbp, 30 mm Cage Plate LED MCPCB-B_Silkscreen.gbo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]
2024-11-21 Working draft of driver circuit
    [15V DC-DC - SRS-1215-2.step, 30 mm Cage Plate LED MCPCB.kicad_sch, BG300-03-X-X-A_REVC.step, D0016A-2.stp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]
2024-11-21 bypass caps added
    [LED controller.kicad_sch]
2024-11-22 Partial PCB layout
    [4689-2520-S-12.stp, 54-00165.STEP, LED controller.kicad_pcb, LED controller.kicad_sch]
2024-11-23 Input jack added
    [LED controller.kicad_pcb, LED controller.kicad_sch, M-RJE3B-188-6X02-N-REVT1.STEP, RJE3A1886102N.STEP]
2024-11-23 Add I/O jack, and re-route
    [LED controller.kicad_pcb, LED controller.kicad_sch]
2024-11-23 more traces added - better grounding
    [LED controller.kicad_pcb, LED controller.kicad_sch]
2024-11-25 All but caps connected
    [LED controller.kicad_pcb, LED controller.kicad_sch]
2024-11-26 All connected - pass DRC
    [LED controller.kicad_pcb, LED controller.kicad_sch]
2024-11-26 Better 18V cap placement
    [LED controller.kicad_pcb]
2024-11-26 Labels added
    [LED controller.kicad_pcb, LED controller.kicad_sch]
2024-11-26 I2C and external LED connector added - Pass DRC
    [LED controller.kicad_pcb, LED controller.kicad_sch]
2024-11-26 Minor changes - ground strip along RJ45 12V, add part # for I2C socket
    [LED controller.kicad_pcb, LED controller.kicad_sch]
2024-11-26 Label schematic - switch to 10-bit DAC
    [LED controller.kicad_pcb, LED controller.kicad_sch]
2024-11-27 Improve clearance of gate traces on LED plate
    [30 mm Cage Plate LED MCPCB.kicad_pcb, 30 mm Cage Plate LED MCPCB.kicad_sch]
2024-12-03 Ordered version
    [30 mm Cage Plate LED MCPCB.csv, 30 mm Cage Plate LED MCPCB.kicad_sch, LED controller.csv]
2024-12-22 CAD model for LED setup
    [30 mm Cage Plate LED MCPCB.kicad_sch, LED controller.kicad_sch, Thorlabs 30 mm Cage Plate LED MCPCB.step]
2025-01-16 Change level shifter IC
    [LED controller.kicad_sch]
2025-01-17 Start porting 4x LED code over - Pin.h done
    [gui_state.obj]
2025-01-17 Fix default therm series resistor
2025-01-23 Add notes for revision to controller board
    [LED controller.kicad_sch]
2025-02-01 Lamda calls can now be looped!
    Using sender() to get the objectName of the sending widget fixes issues with loops and lamda functions
    [gui_state.obj]
2025-02-13 Board boots without errors
2025-02-18 Add single period settling delay on led PWM
    PWM bus appears to need one full period to settle before applying current, otherwise the LED with flash when changing from constant current to PWM.
2025-02-18 Check board disables all 4 LEDs in config
2025-02-20 Fix sync packing, sequence, status window, serial disconnect
    Digital sync is working, sequence tables can now be uploaded, USB disconnects are handled cleanly.
    [12 LED cycle.csv]
2025-02-20 Remove LED offset in initialize Seq since GUI now does offset
2025-03-25 Fix custom sync and sync gui
    [0.1 per PWM OCV.csv, 0.1 per PWM RGB.csv, 80 per PWM OCV.csv, 80 per PWM RGB.csv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]
2025-03-26 Fix status plots and current limits in GUI
    [12 LED cycle.csv, OCV - white balance.csv, RGB - white balance.csv]
2025-04-22 Only pulse the mosfet open for proper current behavior
2025-04-22 Only pulse once at LED off.
2025-07-16 add BOM
    [BOM.xlsx]
2025-07-16 Update pins
    [12 LED cycle.csv, gui_state.obj]
2025-07-16 Add assembly images
2025-07-17 add soldering images
2025-07-17 Clean up Teensy code repository
2025-07-17 Update BOM
    [BOM - Portable Tetrachromatic Display.xlsx, BOM.xlsx]
2025-07-23 Fix Tetrascope display sync
    [80 per PWM OCB.csv]
2025-07-29 Update BOM to red LED
    [BOM - Portable Tetrachromatic Display.xlsx]

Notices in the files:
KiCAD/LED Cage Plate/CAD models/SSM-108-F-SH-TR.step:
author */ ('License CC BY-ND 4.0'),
